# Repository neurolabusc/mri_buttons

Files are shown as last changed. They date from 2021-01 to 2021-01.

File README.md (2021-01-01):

# MRI-compatible buttons

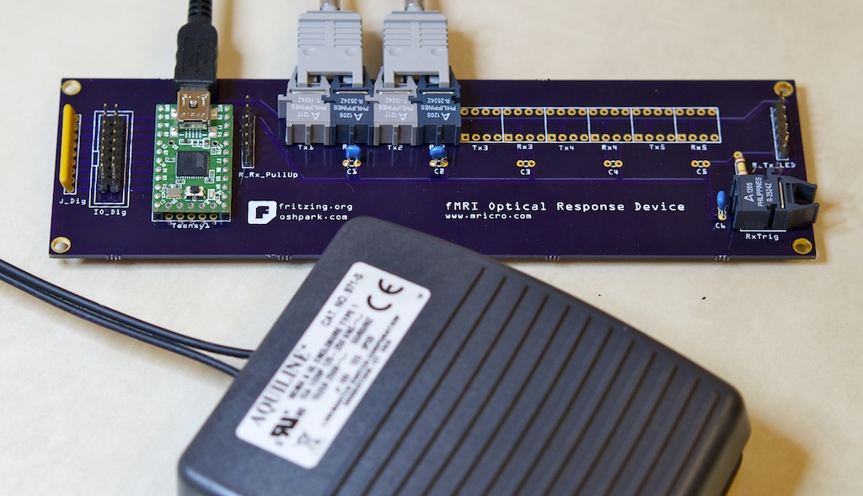
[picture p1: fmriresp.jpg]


During functional magnetic brain imaging we ask participants to conduct cognitive tasks while we scan there brain. The scans are tuned to be sensitive to changes in oxygen levels, so we can infer how the brain works. These studies commonly require us to record the participants responses, to ensure they were completing the task and also to allow us to see if different responses are predicted by different patterns f brain activity - for example what areas of the brain are more active when you remember seeing an item previously versus similar stimuli that you do not remember having seen before? My [DIY fMRI page](https://crnl.readthedocs.io/diy_fmri/index.html) describes a number of professional and home made solutions for collecting button presses in the scanner. As that page notes, there are optical, wireless and wired solutions for this problem. This web page describes an optical-based solution I have built myself. In general, I think most users would be well served with the professional solutions (my work has employed several of these). However, the product I describe here is useful if you have a very tight budget or if you want to build custom input devices (for example I wanted to use foot switches).

## Hardware

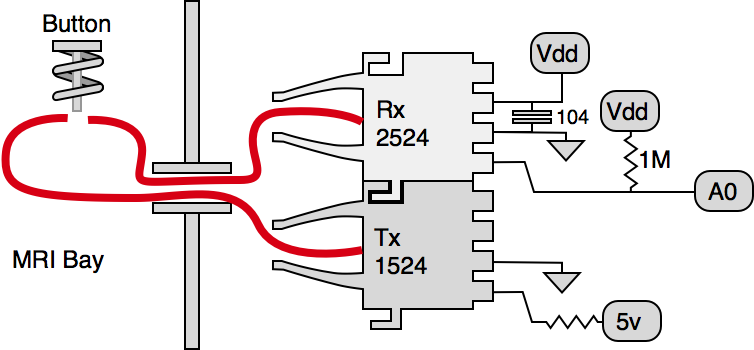
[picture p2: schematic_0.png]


To build this hardware, please download the [Fritzing](https://github.com/fritzing/fritzing-app/releases) plans and Teensy software. You can use Fritzing to generate Gerber files that can be sent for fabrication. This is a very new project, and be aware that these plans differ slightly from the boards I have already built. The new plans should work, but please contact me if you have any issues. schematic.png

My setup allows up to five response buttons - for each button you need to purchase a Avago HFBR-1524 optical transmitter and a Avago HFBR-2524 optical receiver (about $22 a pair). You will also need a Teensy 2.0 ($19), a SIP 5 resistor (6 pin) network of 100 Ohm resistors, a SIP 5 resistor (6 pin) network 330 Ohm resistors, a SIP 5 resistor (6 pin) network of 1M Ohm resistors. For each button, you will need a button and spring assmbly (described below) and a length of VersaLink duplex cable - I purchased a 20-meter patch cable that I cut in half to support two buttons with 10m of length each. You will require one 0.1uF (104) capacitor for each button. You will also need either a large breadboard or a custom printed circuit board (I use OSH Park, but there are many vendors - for example Fritzing in Europe.

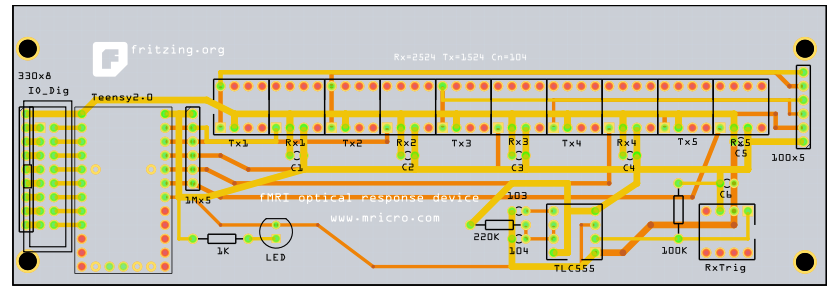
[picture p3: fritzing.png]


To build the device on the printed circuit board (PCB), put the network resistors into the sockets - note that one of the pins connects to ground and this is marked on the resistor with a dot and on the circuit board with a white line. If you put in the network resistors backwards the device will not work. Put the 1OO Ohm resistor in the `R_Tx_LED` socket - these control the power output of the 1524 transmitters. Put the 330 Ohm resistor in the `J_Dig` socket - these allow you to add optional light emitting diodes that will illuminate when a key is pressed. Put the 1M Ohm resistor in the `R_Rx_Pullup` socket - these act as pullup resistors for the 2524 receivers. Put the Teensy 2.0 into the `Teensy` socket. Put each 1524 transmitter into the Tx socket, and each 2524 into the Rx socket. If you only need two buttons fill the sockets with lower numbers (e.g. Tx1, Tx2, Rx1, Rx2). For each receiver, place a 0.1uF (104) decoupling capacitor into the corresponding C1 socket. Now you can plug in your Teensy and upload the software to the Teensy - once this program has been flashed onto the Teensy it will appear as a USB keyboard to any computer you plug it in to. The example.c software I provide is set to support two keys (nKey_A 2), and emulate presses of the 'a' and 'b' keys of a keyboard ({KEY_A, KEY_B}) - simply change these values and recompile if you want to support more buttons or different mappings.

The hardest part of this project is making the non-metal buttons. You will want the button to act as a Guillotine that blocks light from one side of the optical fiber to the other. For foot switches, I adapted the Linemaster 971, replacing the metal spring with a plastic spring, and replacing the mechanical button with a plastic plunger. This works fine - it does not provide a tactile click, but is suitable for a foot pedal. I would be happy to hear and share other creative solutions
